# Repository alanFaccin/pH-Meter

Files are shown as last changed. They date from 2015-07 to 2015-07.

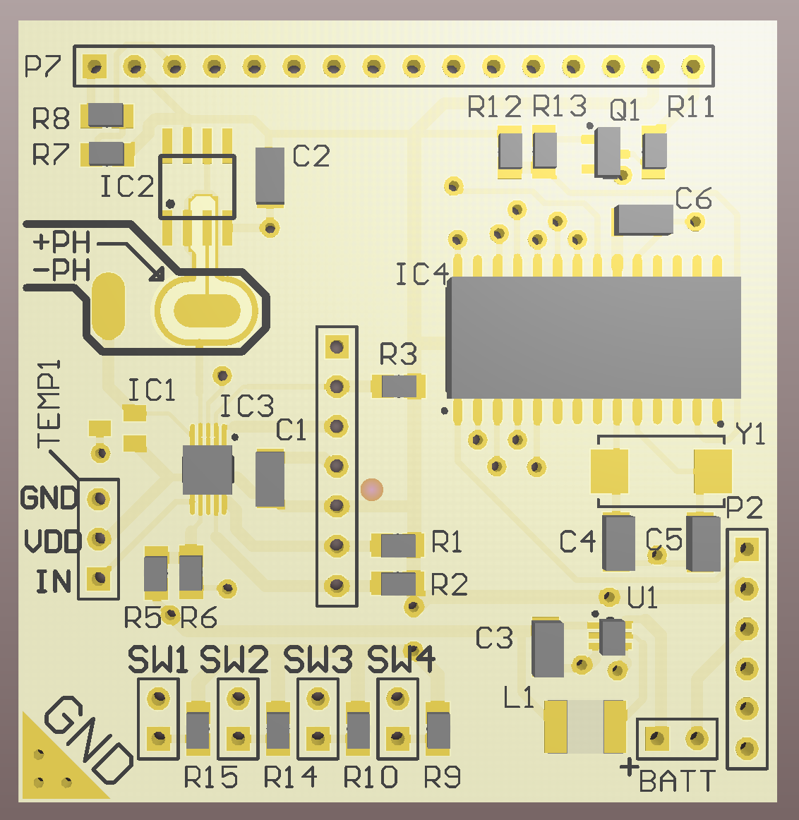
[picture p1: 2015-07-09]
Circuits/export/Schermata 2015-06-11 alle 22.28.34.png

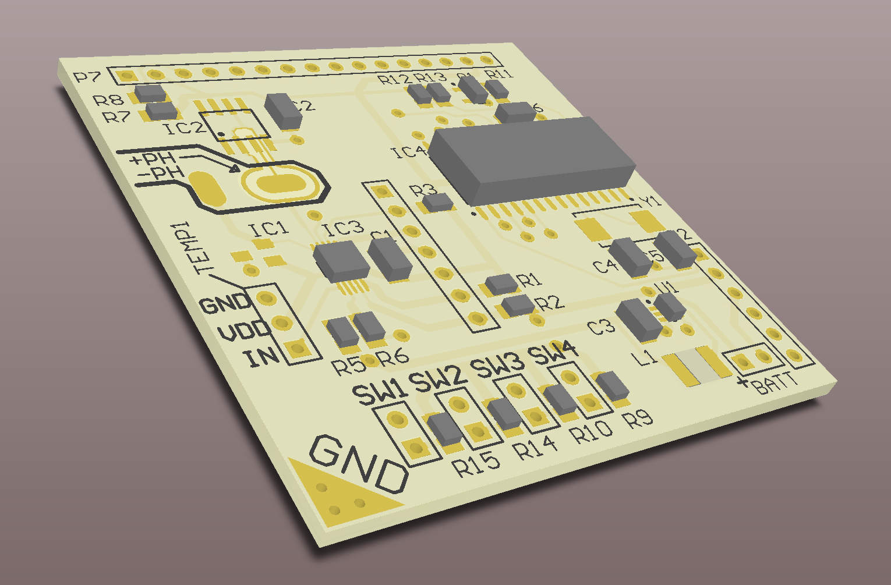
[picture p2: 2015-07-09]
Circuits/export/Schermata 2015-06-11 alle 22.28.52.png

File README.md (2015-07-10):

# pH-Meter

A pH-Meter based on a pic16f876a and a ADS1015 ADC

This project was created as a final year project and thesis.

The purpose of this project is to creare a pH-meter with specifications similar to marketed products.
During development it has been chosen to kept the hardware as modern and concise as possible. When available, modern ICs have been chosen over legacy alternatives, giving space to a state-of-the-art software configurable ADC and ultra-high specs op-amp. [more info in the general hardware description].
The goals of the project were chosen at it’s genesis, and nearly no compromise has been taken during development and design.
An handheld shape has been chosen for the instrument. While a wooden case (CNC machined) is preferred, a 3d printed PLA case is also an available and acceptable solution.

Technical specifications:
• Shape: Handheld tool
• Power source: AA/AAA battery
• Concurrent measurement and display of both pH and temperature • Standard BNC connection for brand-less pH probes
• Temperature resolution better than 0.1°C
• pH resolution of at least 0.1pH
• Easily readable LCD display with firmware control
• Differential measurement mode (delta - Δ)

##license:
A CC-BY-NC-ND Creative Commons license applies

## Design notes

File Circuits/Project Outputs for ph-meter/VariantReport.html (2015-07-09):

Altium customize

# Variant Report

Date | : | 16/06/15
Time | : | 02:15:19
Elapsed Time | : | 00:00:00

## Variations

Physical | Document | Parameter Name | Original Value
C1 | Main_Board.SchDoc | | Fitted
| | Comment
| | Description | Capacitor (Semiconductor SIM Model)
| | Footprint | C1206
| | LatestRevisionDate | 29-May-2009
| | LatestRevisionNote | IPC-7351 Footprint Added.
| | PackageDescription | Chip Capacitor
| | PackageReference | C1206
| | Published | 8-Jun-2000
| | Publisher | Altium Limited
| | Value | 10uF
C2 | Main_Board.SchDoc | | Fitted
| | Comment
| | Description | Capacitor (Semiconductor SIM Model)
| | Footprint | C1206
| | LatestRevisionDate | 29-May-2009
| | LatestRevisionNote | IPC-7351 Footprint Added.
| | PackageDescription | Chip Capacitor
| | PackageReference | C1206
| | Published | 8-Jun-2000
| | Publisher | Altium Limited
| | Value | 10uF
C3 | Main_Board.SchDoc | | Fitted
| | Comment
| | Description | Capacitor (Semiconductor SIM Model)
| | Footprint | C1206
| | LatestRevisionDate | 29-May-2009
| | LatestRevisionNote | IPC-7351 Footprint Added.
| | PackageDescription | Chip Capacitor
| | PackageReference | C1206
| | Published | 8-Jun-2000
| | Publisher | Altium Limited
| | Value | 10uF
C4 | Main_Board.SchDoc | | Fitted
| | Comment
| | Description | Capacitor (Semiconductor SIM Model)
| | Footprint | C1206
| | LatestRevisionDate | 29-May-2009
| | LatestRevisionNote | IPC-7351 Footprint Added.
| | PackageDescription | Chip Capacitor
| | PackageReference | C1206
| | Published | 8-Jun-2000
| | Publisher | Altium Limited
| | Value | 22pF
C5 | Main_Board.SchDoc | | Fitted
| | Comment
| | Description | Capacitor (Semiconductor SIM Model)
| | Footprint | C1206
| | LatestRevisionDate | 29-May-2009
| | LatestRevisionNote | IPC-7351 Footprint Added.
| | PackageDescription | Chip Capacitor
| | PackageReference | C1206
| | Published | 8-Jun-2000
| | Publisher | Altium Limited
| | Value | 22pF
C6 | Main_Board.SchDoc | | Fitted
| | Comment | CAP
| | Description | Capacitor (Semiconductor SIM Model)
| | Footprint | C1206
| | LatestRevisionDate | 29-May-2009
| | LatestRevisionNote | IPC-7351 Footprint Added.
| | PackageDescription | Chip Capacitor
| | PackageReference | C1206
| | Published | 8-Jun-2000
| | Publisher | Altium Limited
| | Value | 100nF
C7 | Main_Board.SchDoc | | Fitted
| | Comment
| | Description | Capacitor (Semiconductor SIM Model)
| | Footprint | C1206
| | LatestRevisionDate | 29-May-2009
| | LatestRevisionNote | IPC-7351 Footprint Added.
| | PackageDescription | Chip Capacitor
| | PackageReference | C1206
| | Published | 8-Jun-2000
| | Publisher | Altium Limited
| | Value | 10uF
H1 | Main_Board.SchDoc | | Fitted
| | Comment | Header 7
| | Description | Header, 7-Pin
| | Footprint | HDR1X7
| | LatestRevisionDate | 17-Jul-2002
| | LatestRevisionNote | Re-released for DXP Platform.
| | Publisher | Altium Limited
IC1 | Main_Board.SchDoc | | Fitted
| | Comment | MAX6101
| | Description | <b> 1.2V Voltage Reference</b> 50ppm/°C, SOT23, 3-Terminal<p> Source: <a href="http://datasheets.maxim-ic.com/en/ds/MAX6520.pdf"> Data sheet </a>
| | Footprint | SOT23
| | MF | MAXIM
| | MPN | MAX6520EUR-T
| | OC_FARNELL | unknown
| | OC_NEWARK | 02J4586
IC2 | Main_Board.SchDoc | | Fitted
| | Comment | LMC6061
| | Description | <b>OP AMP</b>
| | Footprint | SO08
| | V+ | V+
| | V- | V-
IC3 | Main_Board.SchDoc | | Fitted
| | # Input Channels | 4
| | Analog Voltage AV/DD(Max)(V) | 5.5
| | Analog Voltage AV/DD(Min)(V) | 2
| | Architecture | Delta-Sigma
| | Code_JEDEC | MO-153
| | Comment | ADS1015IDGSR
| | ComponentLink1Description | Manufacturer URL
| | ComponentLink1URL | http://www.ti.com/
| | ComponentLink2Description | Datasheet
| | ComponentLink2URL | http://www.ti.com/general/docs/lit/getliterature.tsp?genericPartNumber=ADS1015&fileType=pdf
| | ComponentLink3Description | Package Specification
| | ComponentLink3URL | http://www.ti.com/lit/ml/mpds035b/mpds035b.pdf
| | DatasheetVersion | SBAS473C
| | Description | 12-Bit ADC with Integrated Multiplexer, PGA, Comparator, Oscillator, and Reference, -40 to 125 degC, 10-pin SOP (DGS10), Green (RoHS & no Sb/Br)
| | Digital Supply(Max)(V) | 5.5
| | Digital Supply(Min)(V) | 2
| | Eco-Plan | Green (RoHS & no Sb/Br)
| | Footprint | TI-DGS10_N
| | INL(Max)(+/-LSB) | 0.5
| | Interface | Serial I2C
| | Manufacturer | Texas Instruments
| | Mounting Technology | Surface Mount
| | PackageDescription | 10-Pin Plastic Small Outline, Body 3 x 3 mm, Pitch 0.5 mm
| | PackageReference | DGS10
| | PackageVersion | 4073272/C, 02/2004
| | PartNumber | ADS1015IDGSR
| | Resolution(Bits) | 12
| | Sample Rate (max)(SPS) | 3.3k
| | SubFamily | Precision ADC (<=10MSPS)
| | Supplier 1 | Digi-Key
| | Supplier 2 | Mouser
| | Supplier Part Number 1 | ADS1251U/2K5G4-ND
| | Supplier Part Number 2 | 595-ADS1251U/2K5G4
IC4 | Main_Board.SchDoc | | Fitted
| | # of A/D Channels | 5
| | Comment | PIC16F876-04/SO
| | ComponentLink1Description | Datasheet
| | ComponentLink1URL | http://ww1.microchip.com/downloads/en/DeviceDoc/30292D.pdf
| | ComponentLink2Description | Package Specification
| | ComponentLink2URL | http://www.microchip.com/stellent/groups/techpub_sg/documents/packagingspec/en012702.pdf
| | ComponentLink3Description | URL Link1
| | ComponentLink3URL | Product URL:http://www.microchip.com/datasheet/PIC16F876
| | DatasheetVersion | Rev. D
| | Description | 8-Bit CMOS Flash Microcontroller, 4 MHz, 22 I/O, 0 to 70 degC, 28-pin SOIC (SO28), Tube
| | Digital Communication | 0 -UART, 1 -A/E/USART, 0 -SPI, 0 -I2C, 1 -MSSP(SPI/I2C)
| | EEPROM Data Memory (bytes) | 256
| | Footprint | MCHP-SOIC-SO28_L
| | I/O Pins | 22
| | Manufacturer | Microchip
| | Max. CPU Speed MHz | 4
| | Memory Type | Flash
| | Mounting Technology | Surface Mount
| | Operation Voltage Range | 4V - 5.5V
| | PackageDescription | 28-Lead Plastic Small Outline, 17.9 x 7.5 mm Body, 1.27 mm Pitch
| | PackageReference | SOIC-SO28
| | PackageVersion | C04-052C, 12/2012
| | Packing | TUBE
| | PartNumber | PIC16F876-04/SO
| | Program Memory KBytes | 14
| | Program Memory KWords | 8
| | RAM | 368
| | RoHS | TRUE
| | Supplier 1 | Digi-Key
| | Supplier 2 | Farnell
| | Supplier 3 | Farnell
| | Supplier 4 | Farnell
| | Supplier 5 | Newark
| | Supplier 6 | Mouser
| | Supplier Part Number 1 | PIC16F876-04/SO-ND
| | Supplier Part Number 2 | 9761225MPKG
| | Supplier Part Number 3 | 9761225
| | Supplier Part Number 4 | 1660037
| | Supplier Part Number 5 | 23C5082
| | Supplier Part Number 6 | 579-PIC16F876-04/SO
| | Timers | 2 - 8-bit, 1 - 16-bit
L1 | Main_Board.SchDoc | | Fitted
| | Code_IEC | 1005
| | Code_JEITA | 0402
| | Comment | Inductor
| | Description | Inductor
| | Footprint | INDC4532
| | LatestRevisionDate | 29-May-2009
| | LatestRevisionNote | IPC-7351 Footprint Added.
| | PackageDescription | Chip Inductor
| | PackageReference | 0402-A
| | Published | 8-Jun-2000
| | Publisher | Altium Limited
| | Value | 4.7uH
P1 | Main_Board.SchDoc | | Fitted
| | Comment | Header 2
| | Description | Header, 2-Pin
| | Footprint | HDR1X2
| | LatestRevisionDate | 17-Jul-2002
| | LatestRevisionNote | Re-released for DXP Platform.
| | Publisher | Altium Limited
P2 | Main_Board.SchDoc | | Fitted
| | Comment | Header 6
| | Description | Header, 6-Pin
| | Footprint | HDR1X6
| | LatestRevisionDate | 17-Jul-2002
| | LatestRevisionNote | Re-released for DXP Platform.
| | Publisher | Altium Limited
P3 | Main_Board.SchDoc | | Fitted
| | Comment | Header 2
| | Description | Header, 2-Pin
| | Footprint | HDR1X2
| | LatestRevisionDate | 17-Jul-2002
| | LatestRevisionNote | Re-released for DXP Platform.
| | Publisher | Altium Limited
P4 | Main_Board.SchDoc | | Fitted
| | Comment | Header 2
| | Description | Header, 2-Pin
| | Footprint | HDR1X2
| | LatestRevisionDate | 17-Jul-2002
| | LatestRevisionNote | Re-released for DXP Platform.
| | Publisher | Altium Limited
P5 | Main_Board.SchDoc | | Fitted
| | Comment | Header 2
| | Description | Header, 2-Pin
| | Footprint | HDR1X2
| | LatestRevisionDate | 17-Jul-2002
| | LatestRevisionNote | Re-released for DXP Platform.
| | Publisher | Altium Limited
P6 | Main_Board.SchDoc | | Fitted
| | Comment | Header 2
| | Description | Header, 2-Pin
| | Footprint | HDR1X2
| | LatestRevisionDate | 17-Jul-2002
| | LatestRevisionNote | Re-released for DXP Platform.
| | Publisher | Altium Limited
P7 | Main_Board.SchDoc | | Fitted
| | Comment | Header 16
| | Description | Header, 16-Pin
| | Footprint | HDR1X16
| | LatestRevisionDate | 17-Jul-2002
| | LatestRevisionNote | Re-released for DXP Platform.
| | Publisher | Altium Limited
Q1 | Main_Board.SchDoc | | Fitted
| | Comment | BC846
| | ComponentLink1Description | Manufacturer Link
| | ComponentLink1URL | http://www.semiconductors.philips.com/
| | ComponentLink2Description | Datasheet
| | ComponentLink2URL | http://www.semiconductors.philips.com/acrobat/datasheets/BC846_BC847_BC848_5.pdf
| | DatasheetVersion | 4-Feb-2002
| | Description | NPN General-purpose Transistor
| | Footprint | SOT23_L
| | LatestRevisionDate | 12-Dec-2006
| | LatestRevisionNote | IPC-7351 Footprint Added.
| | PackageDescription | 3-Pin SOT-23 Package 0.95 mm Pitch, 2.3 mm Lead Span
| | PackageReference | SOT23
| | PackageVersion | May-1999
| | Published | 17-Sep-2003
| | Publisher | Altium Limited
R1 | Main_Board.SchDoc | | Fitted
| | Comment | 10K

Description

<p><b>Resistors</b></p> <b>0402</b> - 0402 Surface Mount Package <ul> <li>22 Ohm 1% 1/16W [Digikey: 311-22.0LRTR-ND]</li> <li>33 Ohm 5% 1/16W</li> <li>1.0K 5% 1/16W</li> <li>1.5K 5% 1/16W</li> <li>2.0K 1% 1/16W</li> <li>10.0K 1% 1/16W [Digikey: 311-10.0KLRTR-ND]</li> <li>10.0K 5% 1/16W [Digikey: RMCF0402JT10K0TR-ND]</li> <li>12.1K 1% 1/16W [Digikey: 311-22.0LRTR-ND]</li> <li>100.0K 5% 1/16W</li> </ul> <b>0603</b> - 0603 Surface Mount Package<br> <ul> <li>0 Ohm 1/10 Watt 1% Resistor</li> <li>15 Ohm 1/10 Watt 1% Resistor</li> <li>33 Ohm 1/10 Watt 1% Resistor</li> <li>49.9 Ohm 1/10 Watt 1% Resistor</li> <li>100 Ohm 1/10 Watt 1% Resistor</li> <li>150 Ohm 1/10 Watt 1% Resistor</li> <li>240 Ohm 1/10 Watt 1% Resistor</li> <li>390 Ohm 1/10 Watt 1% Resistor</li> <li>560 Ohm 1/10 Watt 1% Resistor</li> <li>680 Ohm 1/10 Watt 1% Resistor</li> <li>750 Ohm 1/10 Watt 1% Resistor</li> <li>1.0K Ohm 1/10 Watt 1% Resistor</li> <li>1.5K Ohm 1/10 Watt 1% Resistor</li> <li>2.0K Ohm 1/10 Watt 1% Resistor</li> <li>2.2K Ohm 1/10 Watt 1% Resistor</li> <li>3.3K Ohm 1/10 Watt 1% Resistor</li> <li>4.7K Ohm 1/10 Watt 1% Resistor</li> <li>10.0K Ohm 1/10 Watt 1% Resistor</li> <li>12.0K Ohm 1/10 Watt 1% Resistor</li> <li>12.1K Ohm 1/10 Watt 1% Resistor</li> <li>20.0K Ohm 1/10 Watt 1% Resistor</li> <li>33.0K Ohm 1/10 Watt 1% Resistor</li> <li>100.0K Ohm 1/10 Watt 1% Resistor</li> </ul> <b>0805</b> - 0805 Surface Mount Package <ul> <li>0 Ohm 1/8 Watt 1% Resistor</li> <li>33 Ohm 1/8 Watt 1% Resistor</li> <li>100 Ohm 1/8 Watt 1% Resistor</li> <li>150 Ohm 1/8 Watt 1% Resistor</li> <li>200 Ohm 1/8 Watt 1% Resistor</li> <li>240 Ohm 1/8 Watt 1% Resistor</li> <li>330 Ohm 1/8 Watt 1% Resistor</li> <li>390 Ohm 1/8 Watt 1% Resistor</li> <li>470 Ohm 1/8 Watt 1% Resistor</li> <li>1.0K Ohm 1/8 Watt 1% Resistor</li> <li>1.5K Ohm 1/8 Watt 1% Resistor</li> <li>2.0K Ohm 1/8 Watt 1% Resistor</li> <li>4.7K Ohm 1/8 Watt 1% Resistor</li> <li>5.1K Ohm 1/8 Watt 1% Resistor</li> <li>5.6K Ohm 1/8 Watt 1% Resistor</li> <li>10.0K Ohm 1/8 Watt 1% Resistor</li> <li>22.0K Ohm 1/8 Watt 1% Resistor</li> <li>33.0K Ohm 1/8 Watt 1% Resistor</li> <li>100K Ohm 1/8 Watt 1% Resistor</li> </ul> <b>1206</b> - 1206 Surface Mount Package<br/> <br/> <b>2012</b> - 2010 Surface Mount Package<br/> <ul><li>0.11 Ohm 1/2 Watt 1% Resistor - Digikey: RHM.11UCT-ND</li></ul>
| | Footprint | 6-0805_M
R2 | Main_Board.SchDoc | | Fitted
| | Comment | 10K

Description

<p><b>Resistors</b></p> <b>0402</b> - 0402 Surface Mount Package <ul> <li>22 Ohm 1% 1/16W [Digikey: 311-22.0LRTR-ND]</li> <li>33 Ohm 5% 1/16W</li> <li>1.0K 5% 1/16W</li> <li>1.5K 5% 1/16W</li> <li>2.0K 1% 1/16W</li> <li>10.0K 1% 1/16W [Digikey: 311-10.0KLRTR-ND]</li> <li>10.0K 5% 1/16W [Digikey: RMCF0402JT10K0TR-ND]</li> <li>12.1K 1% 1/16W [Digikey: 311-22.0LRTR-ND]</li> <li>100.0K 5% 1/16W</li> </ul> <b>0603</b> - 0603 Surface Mount Package<br> <ul> <li>0 Ohm 1/10 Watt 1% Resistor</li> <li>15 Ohm 1/10 Watt 1% Resistor</li> <li>33 Ohm 1/10 Watt 1% Resistor</li> <li>49.9 Ohm 1/10 Watt 1% Resistor</li> <li>100 Ohm 1/10 Watt 1% Resistor</li> <li>150 Ohm 1/10 Watt 1% Resistor</li> <li>240 Ohm 1/10 Watt 1% Resistor</li> <li>390 Ohm 1/10 Watt 1% Resistor</li> <li>560 Ohm 1/10 Watt 1% Resistor</li> <li>680 Ohm 1/10 Watt 1% Resistor</li> <li>750 Ohm 1/10 Watt 1% Resistor</li> <li>1.0K Ohm 1/10 Watt 1% Resistor</li> <li>1.5K Ohm 1/10 Watt 1% Resistor</li> <li>2.0K Ohm 1/10 Watt 1% Resistor</li> <li>2.2K Ohm 1/10 Watt 1% Resistor</li> <li>3.3K Ohm 1/10 Watt 1% Resistor</li> <li>4.7K Ohm 1/10 Watt 1% Resistor</li> <li>10.0K Ohm 1/10 Watt 1% Resistor</li> <li>12.0K Ohm 1/10 Watt 1% Resistor</li> <li>12.1K Ohm 1/10 Watt 1% Resistor</li> <li>20.0K Ohm 1/10 Watt 1% Resistor</li> <li>33.0K Ohm 1/10 Watt 1% Resistor</li> <li>100.0K Ohm 1/10 Watt 1% Resistor</li> </ul> <b>0805</b> - 0805 Surface Mount Package <ul> <li>0 Ohm 1/8 Watt 1% Resistor</li> <li>33 Ohm 1/8 Watt 1% Resistor</li> <li>100 Ohm 1/8 Watt 1% Resistor</li> <li>150 Ohm 1/8 Watt 1% Resistor</li> <li>200 Ohm 1/8 Watt 1% Resistor</li> <li>240 Ohm 1/8 Watt 1% Resistor</li> <li>330 Ohm 1/8 Watt 1% Resistor</li> <li>390 Ohm 1/8 Watt 1% Resistor</li> <li>470 Ohm 1/8 Watt 1% Resistor</li> <li>1.0K Ohm 1/8 Watt 1% Resistor</li> <li>1.5K Ohm 1/8 Watt 1% Resistor</li> <li>2.0K Ohm 1/8 Watt 1% Resistor</li> <li>4.7K Ohm 1/8 Watt 1% Resistor</li> <li>5.1K Ohm 1/8 Watt 1% Resistor</li> <li>5.6K Ohm 1/8 Watt 1% Resistor</li> <li>10.0K Ohm 1/8 Watt 1% Resistor</li> <li>22.0K Ohm 1/8 Watt 1% Resistor</li> <li>33.0K Ohm 1/8 Watt 1% Resistor</li> <li>100K Ohm 1/8 Watt 1% Resistor</li> </ul> <b>1206</b> - 1206 Surface Mount Package<br/> <br/> <b>2012</b> - 2010 Surface Mount Package<br/> <ul><li>0.11 Ohm 1/2 Watt 1% Resistor - Digikey: RHM.11UCT-ND</li></ul>
| | Footprint | 6-0805_M
R3 | Main_Board.SchDoc | | Fitted
| | Comment | 10K

Description

<p><b>Resistors</b></p> <b>0402</b> - 0402 Surface Mount Package <ul> <li>22 Ohm 1% 1/16W [Digikey: 311-22.0LRTR-ND]</li> <li>33 Ohm 5% 1/16W</li> <li>1.0K 5% 1/16W</li> <li>1.5K 5% 1/16W</li> <li>2.0K 1% 1/16W</li> <li>10.0K 1% 1/16W [Digikey: 311-10.0KLRTR-ND]</li> <li>10.0K 5% 1/16W [Digikey: RMCF0402JT10K0TR-ND]</li> <li>12.1K 1% 1/16W [Digikey: 311-22.0LRTR-ND]</li> <li>100.0K 5% 1/16W</li> </ul> <b>0603</b> - 0603 Surface Mount Package<br> <ul> <li>0 Ohm 1/10 Watt 1% Resistor</li> <li>15 Ohm 1/10 Watt 1% Resistor</li> <li>33 Ohm 1/10 Watt 1% Resistor</li> <li>49.9 Ohm 1/10 Watt 1% Resistor</li> <li>100 Ohm 1/10 Watt 1% Resistor</li> <li>150 Ohm 1/10 Watt 1% Resistor</li> <li>240 Ohm 1/10 Watt 1% Resistor</li> <li>390 Ohm 1/10 Watt 1% Resistor</li> <li>560 Ohm 1/10 Watt 1% Resistor</li> <li>680 Ohm 1/10 Watt 1% Resistor</li> <li>750 Ohm 1/10 Watt 1% Resistor</li> <li>1.0K Ohm 1/10 Watt 1% Resistor</li> <li>1.5K Ohm 1/10 Watt 1% Resistor</li> <li>2.0K Ohm 1/10 Watt 1% Resistor</li> <li>2.2K Ohm 1/10 Watt 1% Resistor</li> <li>3.3K Ohm 1/10 Watt 1% Resistor</li> <li>4.7K Ohm 1/10 Watt 1% Resistor</li> <li>10.0K Ohm 1/10 Watt 1% Resistor</li> <li>12.0K Ohm 1/10 Watt 1% Resistor</li> <li>12.1K Ohm 1/10 Watt 1% Resistor</li> <li>20.0K Ohm 1/10 Watt 1% Resistor</li> <li>33.0K Ohm 1/10 Watt 1% Resistor</li> <li>100.0K Ohm 1/10 Watt 1% Resistor</li> </ul> <b>0805</b> - 0805 Surface Mount Package <ul> <li>0 Ohm 1/8 Watt 1% Resistor</li> <li>33 Ohm 1/8 Watt 1% Resistor</li> <li>100 Ohm 1/8 Watt 1% Resistor</li> <li>150 Ohm 1/8 Watt 1% Resistor</li> <li>200 Ohm 1/8 Watt 1% Resistor</li> <li>240 Ohm 1/8 Watt 1% Resistor</li> <li>330 Ohm 1/8 Watt 1% Resistor</li> <li>390 Ohm 1/8 Watt 1% Resistor</li> <li>470 Ohm 1/8 Watt 1% Resistor</li> <li>1.0K Ohm 1/8 Watt 1% Resistor</li> <li>1.5K Ohm 1/8 Watt 1% Resistor</li> <li>2.0K Ohm 1/8 Watt 1% Resistor</li> <li>4.7K Ohm 1/8 Watt 1% Resistor</li> <li>5.1K Ohm 1/8 Watt 1% Resistor</li> <li>5.6K Ohm 1/8 Watt 1% Resistor</li> <li>10.0K Ohm 1/8 Watt 1% Resistor</li> <li>22.0K Ohm 1/8 Watt 1% Resistor</li> <li>33.0K Ohm 1/8 Watt 1% Resistor</li> <li>100K Ohm 1/8 Watt 1% Resistor</li> </ul> <b>1206</b> - 1206 Surface Mount Package<br/> <br/> <b>2012</b> - 2010 Surface Mount Package<br/> <ul><li>0.11 Ohm 1/2 Watt 1% Resistor - Digikey: RHM.11UCT-ND</li></ul>
| | Footprint | 6-0805_M
R5 | Main_Board.SchDoc | | Fitted
| | Comment | 10K

Description

<p><b>Resistors</b></p> <b>0402</b> - 0402 Surface Mount Package <ul> <li>22 Ohm 1% 1/16W [Digikey: 311-22.0LRTR-ND]</li> <li>33 Ohm 5% 1/16W</li> <li>1.0K 5% 1/16W</li> <li>1.5K 5% 1/16W</li> <li>2.0K 1% 1/16W</li> <li>10.0K 1% 1/16W [Digikey: 311-10.0KLRTR-ND]</li> <li>10.0K 5% 1/16W [Digikey: RMCF0402JT10K0TR-ND]</li> <li>12.1K 1% 1/16W [Digikey: 311-22.0LRTR-ND]</li> <li>100.0K 5% 1/16W</li> </ul> <b>0603</b> - 0603 Surface Mount Package<br> <ul> <li>0 Ohm 1/10 Watt 1% Resistor</li> <li>15 Ohm 1/10 Watt 1% Resistor</li> <li>33 Ohm 1/10 Watt 1% Resistor</li> <li>49.9 Ohm 1/10 Watt 1% Resistor</li> <li>100 Ohm 1/10 Watt 1% Resistor</li> <li>150 Ohm 1/10 Watt 1% Resistor</li> <li>240 Ohm 1/10 Watt 1% Resistor</li> <li>390 Ohm 1/10 Watt 1% Resistor</li> <li>560 Ohm 1/10 Watt 1% Resistor</li> <li>680 Ohm 1/10 Watt 1% Resistor</li> <li>750 Ohm 1/10 Watt 1% Resistor</li> <li>1.0K Ohm 1/10 Watt 1% Resistor</li> <li>1.5K Ohm 1/10 Watt 1% Resistor</li> <li>2.0K Ohm 1/10 Watt 1% Resistor</li> <li>2.2K Ohm 1/10 Watt 1% Resistor</li> <li>3.3K Ohm 1/10 Watt 1% Resistor</li> <li>4.7K Ohm 1/10 Watt 1% Resistor</li> <li>10.0K Ohm 1/10 Watt 1% Resistor</li> <li>12.0K Ohm 1/10 Watt 1% Resistor</li> <li>12.1K Ohm 1/10 Watt 1% Resistor</li> <li>20.0K Ohm 1/10 Watt 1% Resistor</li> <li>33.0K Ohm 1/10 Watt 1% Resistor</li> <li>100.0K Ohm 1/10 Watt 1% Resistor</li> </ul> <b>0805</b> - 0805 Surface Mount Package <ul> <li>0 Ohm 1/8 Watt 1% Resistor</li> <li>33 Ohm 1/8 Watt 1% Resistor</li> <li>100 Ohm 1/8 Watt 1% Resistor</li> <li>150 Ohm 1/8 Watt 1% Resistor</li> <li>200 Ohm 1/8 Watt 1% Resistor</li> <li>240 Ohm 1/8 Watt 1% Resistor</li> <li>330 Ohm 1/8 Watt 1% Resistor</li> <li>390 Ohm 1/8 Watt 1% Resistor</li> <li>470 Ohm 1/8 Watt 1% Resistor</li> <li>1.0K Ohm 1/8 Watt 1% Resistor</li> <li>1.5K Ohm 1/8 Watt 1% Resistor</li> <li>2.0K Ohm 1/8 Watt 1% Resistor</li> <li>4.7K Ohm 1/8 Watt 1% Resistor</li> <li>5.1K Ohm 1/8 Watt 1% Resistor</li> <li>5.6K Ohm 1/8 Watt 1% Resistor</li> <li>10.0K Ohm 1/8 Watt 1% Resistor</li> <li>22.0K Ohm 1/8 Watt 1% Resistor</li> <li>33.0K Ohm 1/8 Watt 1% Resistor</li> <li>100K Ohm 1/8 Watt 1% Resistor</li> </ul> <b>1206</b> - 1206 Surface Mount Package<br/> <br/> <b>2012</b> - 2010 Surface Mount Package<br/> <ul><li>0.11 Ohm 1/2 Watt 1% Resistor - Digikey: RHM.11UCT-ND</li></ul>
| | Footprint | 6-0805_M
R6 | Main_Board.SchDoc | | Fitted
| | Comment | 1K

Description

<p><b>Resistors</b></p> <b>0402</b> - 0402 Surface Mount Package <ul> <li>22 Ohm 1% 1/16W [Digikey: 311-22.0LRTR-ND]</li> <li>33 Ohm 5% 1/16W</li> <li>1.0K 5% 1/16W</li> <li>1.5K 5% 1/16W</li> <li>2.0K 1% 1/16W</li> <li>10.0K 1% 1/16W [Digikey: 311-10.0KLRTR-ND]</li> <li>10.0K 5% 1/16W [Digikey: RMCF0402JT10K0TR-ND]</li> <li>12.1K 1% 1/16W [Digikey: 311-22.0LRTR-ND]</li> <li>100.0K 5% 1/16W</li> </ul> <b>0603</b> - 0603 Surface Mount Package<br> <ul> <li>0 Ohm 1/10 Watt 1% Resistor</li> <li>15 Ohm 1/10 Watt 1% Resistor</li> <li>33 Ohm 1/10 Watt 1% Resistor</li> <li>49.9 Ohm 1/10 Watt 1% Resistor</li> <li>100 Ohm 1/10 Watt 1% Resistor</li> <li>150 Ohm 1/10 Watt 1% Resistor</li> <li>240 Ohm 1/10 Watt 1% Resistor</li> <li>390 Ohm 1/10 Watt 1% Resistor</li> <li>560 Ohm 1/10 Watt 1% Resistor</li> <li>680 Ohm 1/10 Watt 1% Resistor</li> <li>750 Ohm 1/10 Watt 1% Resistor</li> <li>1.0K Ohm 1/10 Watt 1% Resistor</li> <li>1.5K Ohm 1/10 Watt 1% Resistor</li> <li>2.0K Ohm 1/10 Watt 1% Resistor</li> <li>2.2K Ohm 1/10 Watt 1% Resistor</li> <li>3.3K Ohm 1/10 Watt 1% Resistor</li> <li>4.7K Ohm 1/10 Watt 1% Resistor</li> <li>10.0K Ohm 1/10 Watt 1% Resistor</li> <li>12.0K Ohm 1/10 Watt 1% Resistor</li> <li>12.1K Ohm 1/10 Watt 1% Resistor</li> <li>20.0K Ohm 1/10 Watt 1% Resistor</li> <li>33.0K Ohm 1/10 Watt 1% Resistor</li> <li>100.0K Ohm 1/10 Watt 1% Resistor</li> </ul> <b>0805</b> - 0805 Surface Mount Package <ul> <li>0 Ohm 1/8 Watt 1% Resistor</li> <li>33 Ohm 1/8 Watt 1% Resistor</li> <li>100 Ohm 1/8 Watt 1% Resistor</li> <li>150 Ohm 1/8 Watt 1% Resistor</li> <li>200 Ohm 1/8 Watt 1% Resistor</li> <li>240 Ohm 1/8 Watt 1% Resistor</li> <li>330 Ohm 1/8 Watt 1% Resistor</li> <li>390 Ohm 1/8 Watt 1% Resistor</li> <li>470 Ohm 1/8 Watt 1% Resistor</li> <li>1.0K Ohm 1/8 Watt 1% Resistor</li> <li>1.5K Ohm 1/8 Watt 1% Resistor</li> <li>2.0K Ohm 1/8 Watt 1% Resistor</li> <li>4.7K Ohm 1/8 Watt 1% Resistor</li> <li>5.1K Ohm 1/8 Watt 1% Resistor</li> <li>5.6K Ohm 1/8 Watt 1% Resistor</li> <li>10.0K Ohm 1/8 Watt 1% Resistor</li> <li>22.0K Ohm 1/8 Watt 1% Resistor</li> <li>33.0K Ohm 1/8 Watt 1% Resistor</li> <li>100K Ohm 1/8 Watt 1% Resistor</li> </ul> <b>1206</b> - 1206 Surface Mount Package<br/> <br/> <b>2012</b> - 2010 Surface Mount Package<br/> <ul><li>0.11 Ohm 1/2 Watt 1% Resistor - Digikey: RHM.11UCT-ND</li></ul>
| | Footprint | 6-0805_M
R7 | Main_Board.SchDoc | | Fitted
| | Comment | Res3
| | Description | Resistor
| | Footprint | 6-0805_M
| | LatestRevisionDate | 29-May-2009
| | LatestRevisionNote | IPC-7351 Footprint Added.
| | PackageDescription | Chip Resistor
| | PackageReference | J1-0603
| | Published | 8-Jun-2000
| | Publisher | Altium Limited
| | Value | 4K7
R8 | Main_Board.SchDoc | | Fitted
| | Comment | Res3
| | Description | Resistor
| | Footprint | 6-0805_M
| | LatestRevisionDate | 29-May-2009
| | LatestRevisionNote | IPC-7351 Footprint Added.
| | PackageDescription | Chip Resistor
| | PackageReference | J1-0603
| | Published | 8-Jun-2000
| | Publisher | Altium Limited
| | Value | 1K
R9 | Main_Board.SchDoc | | Fitted
| | Comment | Res3
| | Description | Resistor
| | Footprint | 6-0805_M
| | LatestRevisionDate | 29-May-2009
| | LatestRevisionNote | IPC-7351 Footprint Added.
| | PackageDescription | Chip Resistor
| | PackageReference | J1-0603
| | Published | 8-Jun-2000
| | Publisher | Altium Limited
| | Value | 10K
R10 | Main_Board.SchDoc | | Fitted
| | Comment | Res3
| | Description | Resistor
| | Footprint | 6-0805_M
| | LatestRevisionDate | 29-May-2009
| | LatestRevisionNote | IPC-7351 Footprint Added.
| | PackageDescription | Chip Resistor
| | PackageReference | J1-0603
| | Published | 8-Jun-2000
| | Publisher | Altium Limited
| | Value | 10K
R11 | Main_Board.SchDoc | | Fitted
| | Comment | Res3
| | Description | Resistor
| | Footprint | 6-0805_M
| | LatestRevisionDate | 29-May-2009
| | LatestRevisionNote | IPC-7351 Footprint Added.
| | PackageDescription | Chip Resistor
| | PackageReference | J1-0603
| | Published | 8-Jun-2000
| | Publisher | Altium Limited
| | Value | 56
R12 | Main_Board.SchDoc | | Fitted
| | Comment | Res3
| | Description | Resistor
| | Footprint | 6-0805_M
| | LatestRevisionDate | 29-May-2009
| | LatestRevisionNote | IPC-7351 Footprint Added.
| | PackageDescription | Chip Resistor
| | PackageReference | J1-0603
| | Published | 8-Jun-2000
| | Publisher | Altium Limited
| | Value | 1K
R13 | Main_Board.SchDoc | | Fitted
| | Comment | Res3
| | Description | Resistor
| | Footprint | 6-0805_M
| | LatestRevisionDate | 29-May-2009
| | LatestRevisionNote | IPC-7351 Footprint Added.
| | PackageDescription | Chip Resistor
| | PackageReference | J1-0603
| | Published | 8-Jun-2000
| | Publisher | Altium Limited
| | Value | 4K7
R14 | Main_Board.SchDoc | | Fitted
| | Comment | Res3
| | Description | Resistor
| | Footprint | 6-0805_M
| | LatestRevisionDate | 29-May-2009
| | LatestRevisionNote | IPC-7351 Footprint Added.
| | PackageDescription | Chip Resistor
| | PackageReference | J1-0603
| | Published | 8-Jun-2000
| | Publisher | Altium Limited
| | Value | 10K
R15 | Main_Board.SchDoc | | Fitted
| | Comment | Res3
| | Description | Resistor
| | Footprint | 6-0805_M
| | LatestRevisionDate | 29-May-2009
| | LatestRevisionNote | IPC-7351 Footprint Added.
| | PackageDescription | Chip Resistor
| | PackageReference | J1-0603
| | Published | 8-Jun-2000
| | Publisher | Altium Limited
| | Value | 10K
S1 | Main_Board.SchDoc | | Fitted
| | Comment | SW-PB
| | Description | Switch
| | Footprint
| | LatestRevisionDate | 17-Jul-2002
| | LatestRevisionNote | Re-released for DXP Platform.
| | PackageDescription | Switch; 2 Leads
| | PackageReference | SPST-2
| | Published | 24-Mar-1999
| | Publisher | Altium Limited
S2 | Main_Board.SchDoc | | Fitted
| | Comment | SW-PB
| | Description | Switch
| | Footprint
| | LatestRevisionDate | 17-Jul-2002
| | LatestRevisionNote | Re-released for DXP Platform.
| | PackageDescription | Switch; 2 Leads
| | PackageReference | SPST-2
| | Published | 24-Mar-1999
| | Publisher | Altium Limited
S3 | Main_Board.SchDoc | | Fitted
| | Comment | SW-PB
| | Description | Switch
| | Footprint
| | LatestRevisionDate | 17-Jul-2002
| | LatestRevisionNote | Re-released for DXP Platform.
| | PackageDescription | Switch; 2 Leads
| | PackageReference | SPST-2
| | Published | 24-Mar-1999
| | Publisher | Altium Limited
S4 | Main_Board.SchDoc | | Fitted
| | Comment | SW-PB
| | Description | Switch
| | Footprint
| | LatestRevisionDate | 17-Jul-2002
| | LatestRevisionNote | Re-released for DXP Platform.
| | PackageDescription | Switch; 2 Leads
| | PackageReference | SPST-2
| | Published | 24-Mar-1999
| | Publisher | Altium Limited
TEMP1 | Main_Board.SchDoc | | Fitted
| | Comment | Header 3
| | Description | Header, 3-Pin
| | Footprint | HDR1X3
| | LatestRevisionDate | 17-Jul-2002
| | LatestRevisionNote | Re-released for DXP Platform.
| | Publisher | Altium Limited
U1 | Main_Board.SchDoc | | Fitted
| | Code_JEDEC | MO-203-AB
| | Comment | TPS61222DCKR
| | ComponentLink1Description | Datasheet
| | ComponentLink1URL | http://www.ti.com/general/docs/lit/getliterature.tsp?genericPartNumber=TPS61222&fileType=pdf
| | ComponentLink2Description | Package Specification
| | ComponentLink2URL | http://www.ti.com/litv/pdf/mpds114c
| | DatasheetVersion | SLVS776
| | Description | Boost Voltage Converter with 0.7 to 5.5 V Input and 5 V Output, -40 to 85 degC, 6-Pin SC70 (DCK), Green (RoHS & no Sb/Br)
| | Eco-Plan | Green (RoHS & no Sb/Br)
| | Footprint | DCK6_N
| | Manufacturer | Texas Instruments
| | Mounting Technology | Surface Mount
| | PackageDescription | 6-Pin Plastic Small-Outline Package, 2 x 1.3 mm Body, 0.65 mm Pitch, 2.1 mm Lead Span
| | PackageReference | DCK6
| | PackageVersion | revG, Jan-2007
| | PartNumber | TPS61222DCKR
| | Regulated Outputs(#) | 1
| | SubFamily | Step-Up Regulator
| | Supplier 1 | Digi-Key
| | Supplier 2 | Newark
| | Supplier 3 | Mouser
| | Supplier Part Number 1 | TPS61222DCKR-ND
| | Supplier Part Number 2 | 09R6667
| | Supplier Part Number 3 | 595-TPS61222DCKR
| | Switching Frequency(Max)(kHz) | 2000
| | Topology | Boost
| | Vin(Max)(V) | 5.5
| | Vin(Min)(V) | 0.7
| | Vout(Max)(V) | 5
| | Vout(Min)(V) | 5
Y1 | Main_Board.SchDoc | | Fitted
| | Comment | 16Mhz
| | ComponentLink1Description | Manufacturer Link
| | ComponentLink1URL | http://www.cmac.com/mt/
| | ComponentLink2Description | Datasheet
| | ComponentLink2URL | http://www.cmac.com/mt/databook/crystals/smd/3smx.pdf
| | DatasheetDocument | 6-Apr-1998
| | Description | Surface Mount Quartz Crystal
| | Footprint | CFPX-93
| | Note | PCB layout complies with manufacturer's recommendation.
| | PackageDocument | 6-Apr-1998
| | PackageReference | 3SMXA
| | Published | 17-Jul-2002
| | Publisher | Altium Limited

Back to top

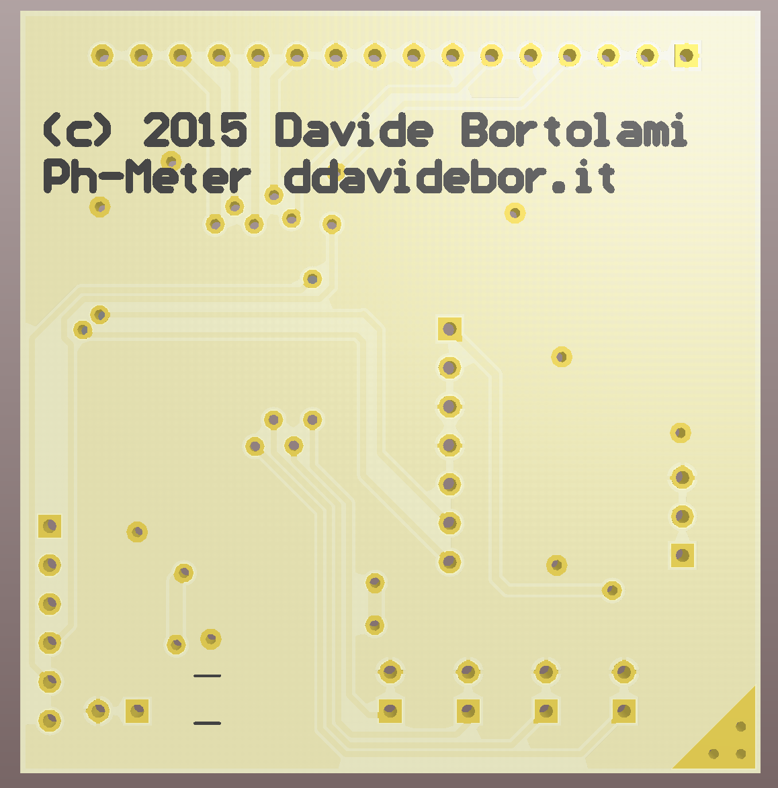
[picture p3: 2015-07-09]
Circuits/export/Schermata 2015-06-11 alle 22.29.11.png

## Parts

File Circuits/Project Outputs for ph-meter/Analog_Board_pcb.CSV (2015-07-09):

Bill of Material for
On 11/06/15 at 22:24:15
Comment | Pattern | Quantity | Components
 | C1206 | 5 | C1, C2, C3, C4, C5 | Capacitor (Semiconductor SIM Model)
10K | 6-0805_M | 4 | R1, R2, R3, R5 | <p><b>Resistors</b></p> <b>0402</b> - 0402 Surface Mount Package <ul> <li>22 Ohm 1% 1/16W [Digikey: 311-22.0LRTR-ND]</li> <li>33 Ohm 5% 1/16W</li> <li>1.0K 5% 1/16W</li> <li>1.5K 5% 1/16W</li> <li>2.0K 1% 1/16W</li> <li>10.0K 1% 1/16W [Digikey: 311-10.0KLRTR-ND]</li> <li>10.0K 5% 1/16W [Digikey: RMCF0402JT10K0TR-ND]</li> <li>12.1K 1% 1/16W [Digikey: 311-22.0LRTR-ND]</li> <li>100.0K 5% 1/16W</li> </ul> <b>0603</b> - 0603 Surface Mount Package<br> <ul> <li>0 Ohm 1/10 Watt 1% Resistor</li> <li>15 Ohm 1/10 Watt 1% Resistor</li> <li>33 Ohm 1/10 Watt 1% Resistor</li> <li>49.9 Ohm 1/10 Watt 1% Resistor</li> <li>100 Ohm 1/10 Watt 1% Resistor</li> <li>150 Ohm 1/10 Watt 1% Resistor</li> <li>240 Ohm 1/10 Watt 1% Resistor</li> <li>390 Ohm 1/10 Watt 1% Resistor</li> <li>560 Ohm 1/10 Watt 1% Resistor</li> <li>680 Ohm 1/10 Watt 1% Resistor</li> <li>750 Ohm 1/10 Watt 1% Resistor</li> <li>1.0K Ohm 1/10 Watt 1% Resistor</li> <li>1.5K Ohm 1/10 Watt 1% Resistor</li> <li>2.0K Ohm 1/10 Watt 1% Resistor</li> <li>2.2K Ohm 1/10 Watt 1% Resistor</li> <li>3.3K Ohm 1/10 Watt 1% Resistor</li> <li>4.7K Ohm 1/10 Watt 1% Resistor</li> <li>10.0K Ohm 1/10 Watt 1% Resistor</li> <li>12.0K Ohm 1/10 Watt 1% Resistor</li> <li>12.1K Ohm 1/10 Watt 1% Resistor</li> <li>20.0K Ohm 1/10 Watt 1% Resistor</li> <li>33.0K Ohm 1/10 Watt 1% Resistor</li> <li>100.0K Ohm 1/10 Watt 1% Resistor</li> </ul> <b>0805</b> - 0805 Surface Mount Package <ul> <li>0 Ohm 1/8 Watt 1% Resistor</li> <li>33 Ohm 1/8 Watt 1% Resistor</li> <li>1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
16Mhz | CFPX-93 | 1 | Y1 | Surface Mount Quartz Crystal
1K | 6-0805_M | 1 | R6 | <p><b>Resistors</b></p> <b>0402</b> - 0402 Surface Mount Package <ul> <li>22 Ohm 1% 1/16W [Digikey: 311-22.0LRTR-ND]</li> <li>33 Ohm 5% 1/16W</li> <li>1.0K 5% 1/16W</li> <li>1.5K 5% 1/16W</li> <li>2.0K 1% 1/16W</li> <li>10.0K 1% 1/16W [Digikey: 311-10.0KLRTR-ND]</li> <li>10.0K 5% 1/16W [Digikey: RMCF0402JT10K0TR-ND]</li> <li>12.1K 1% 1/16W [Digikey: 311-22.0LRTR-ND]</li> <li>100.0K 5% 1/16W</li> </ul> <b>0603</b> - 0603 Surface Mount Package<br> <ul> <li>0 Ohm 1/10 Watt 1% Resistor</li> <li>15 Ohm 1/10 Watt 1% Resistor</li> <li>33 Ohm 1/10 Watt 1% Resistor</li> <li>49.9 Ohm 1/10 Watt 1% Resistor</li> <li>100 Ohm 1/10 Watt 1% Resistor</li> <li>150 Ohm 1/10 Watt 1% Resistor</li> <li>240 Ohm 1/10 Watt 1% Resistor</li> <li>390 Ohm 1/10 Watt 1% Resistor</li> <li>560 Ohm 1/10 Watt 1% Resistor</li> <li>680 Ohm 1/10 Watt 1% Resistor</li> <li>750 Ohm 1/10 Watt 1% Resistor</li> <li>1.0K Ohm 1/10 Watt 1% Resistor</li> <li>1.5K Ohm 1/10 Watt 1% Resistor</li> <li>2.0K Ohm 1/10 Watt 1% Resistor</li> <li>2.2K Ohm 1/10 Watt 1% Resistor</li> <li>3.3K Ohm 1/10 Watt 1% Resistor</li> <li>4.7K Ohm 1/10 Watt 1% Resistor</li> <li>10.0K Ohm 1/10 Watt 1% Resistor</li> <li>12.0K Ohm 1/10 Watt 1% Resistor</li> <li>12.1K Ohm 1/10 Watt 1% Resistor</li> <li>20.0K Ohm 1/10 Watt 1% Resistor</li> <li>33.0K Ohm 1/10 Watt 1% Resistor</li> <li>100.0K Ohm 1/10 Watt 1% Resistor</li> </ul> <b>0805</b> - 0805 Surface Mount Package <ul> <li>0 Ohm 1/8 Watt 1% Resistor</li> <li>33 Ohm 1/8 Watt 1% Resistor</li> <li>1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
ADS1015IDGSR | TI-DGS10_N | 1 | IC3 | 12-Bit ADC with Integrated Multiplexer, PGA, Comparator, Oscillator, and Reference, -40 to 125 degC, 10-pin SOP (DGS10), Green (RoHS & no Sb/Br)
BC846 | SOT23_L | 1 | Q1 | NPN General-purpose Transistor
Cap Semi | C1206 | 1 | C6 | Capacitor (Semiconductor SIM Model)
Header 16 | HDR1X16 | 1 | P7 | Header, 16-Pin
Header 2 | HDR1X2 | 5 | BATT, SW1, SW2, SW3, SW4 | Header, 2-Pin
Header 3 | HDR1X3 | 1 | TEMP1 | Header, 3-Pin
Header 6 | HDR1X6 | 1 | P2 | Header, 6-Pin
Header 7 | HDR1X7 | 1 | H1 | Header, 7-Pin
Inductor | INDC4532 | 1 | L1 | Inductor
LMC6061 | SO08 | 1 | IC2 | <b>OP AMP</b>
MAX6101 | SOT23 | 1 | IC1 | <b> 1.2V Voltage Reference</b> 50ppm/°C, SOT23, 3-Terminal<p> Source: <a href=http://datasheets.maxim-ic.com/en/ds/MAX6520.pdf"> Data sheet </a>"
PIC16F876-04/SO | MCHP-SOIC-SO28_L | 1 | IC4 | 8-Bit CMOS Flash Microcontroller, 4 MHz, 22 I/O, 0 to 70 degC, 28-pin SOIC (SO28), Tube
Res3 | 6-0805_M | 9 | R7, R8, R9, R10, R11, R12, R13, R14, R15 | Resistor
TPS61222DCKR | DCK6_N | 1 | U1 | Boost Voltage Converter with 0.7 to 5.5 V Input and 5 V Output, -40 to 85 degC, 6-Pin SC70 (DCK), Green (RoHS & no Sb/Br)

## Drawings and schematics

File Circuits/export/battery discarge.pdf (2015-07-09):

Constant Power Performance | Constant Current Performance

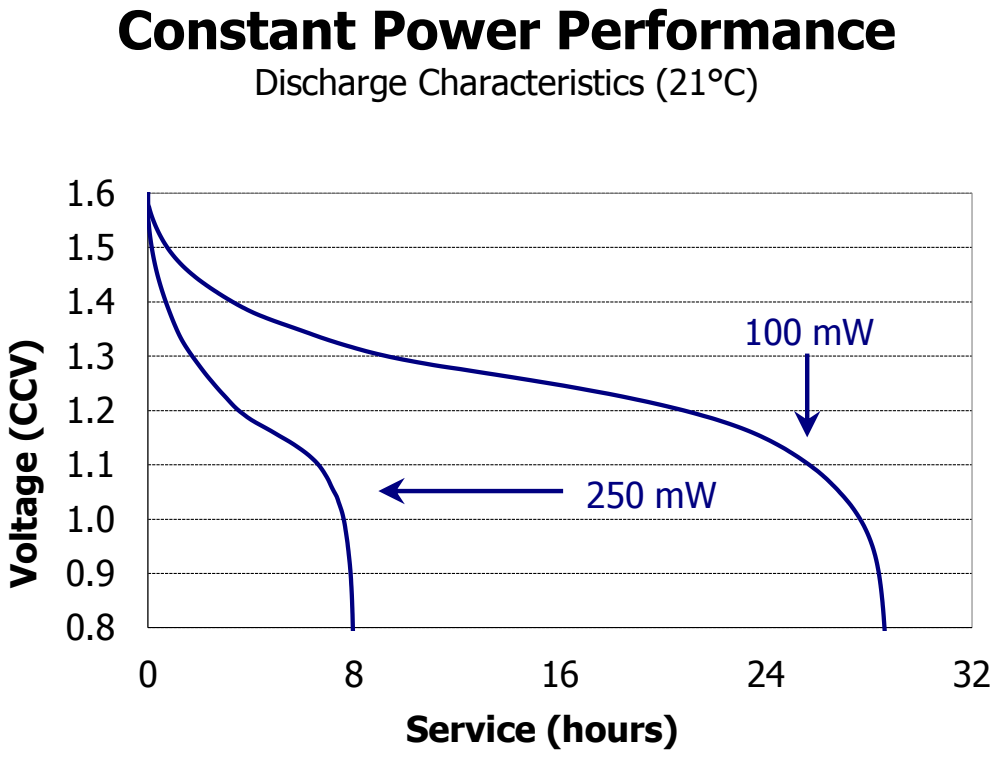
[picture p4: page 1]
Discharge Characteristics (21°C); Voltage (CCV); Service (hours)

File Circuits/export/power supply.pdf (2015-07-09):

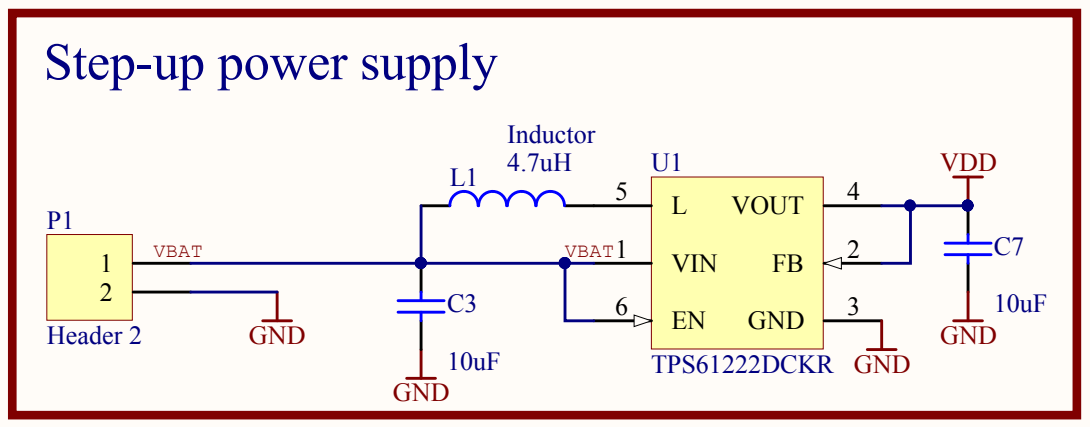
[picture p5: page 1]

Step-up power supply

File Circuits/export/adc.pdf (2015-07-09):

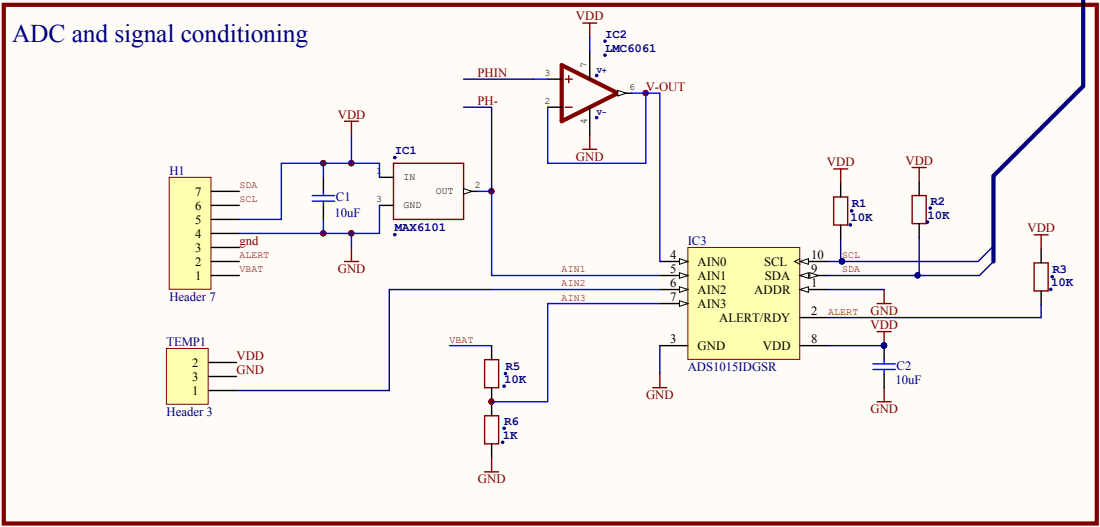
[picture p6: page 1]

ADC and signal conditioning

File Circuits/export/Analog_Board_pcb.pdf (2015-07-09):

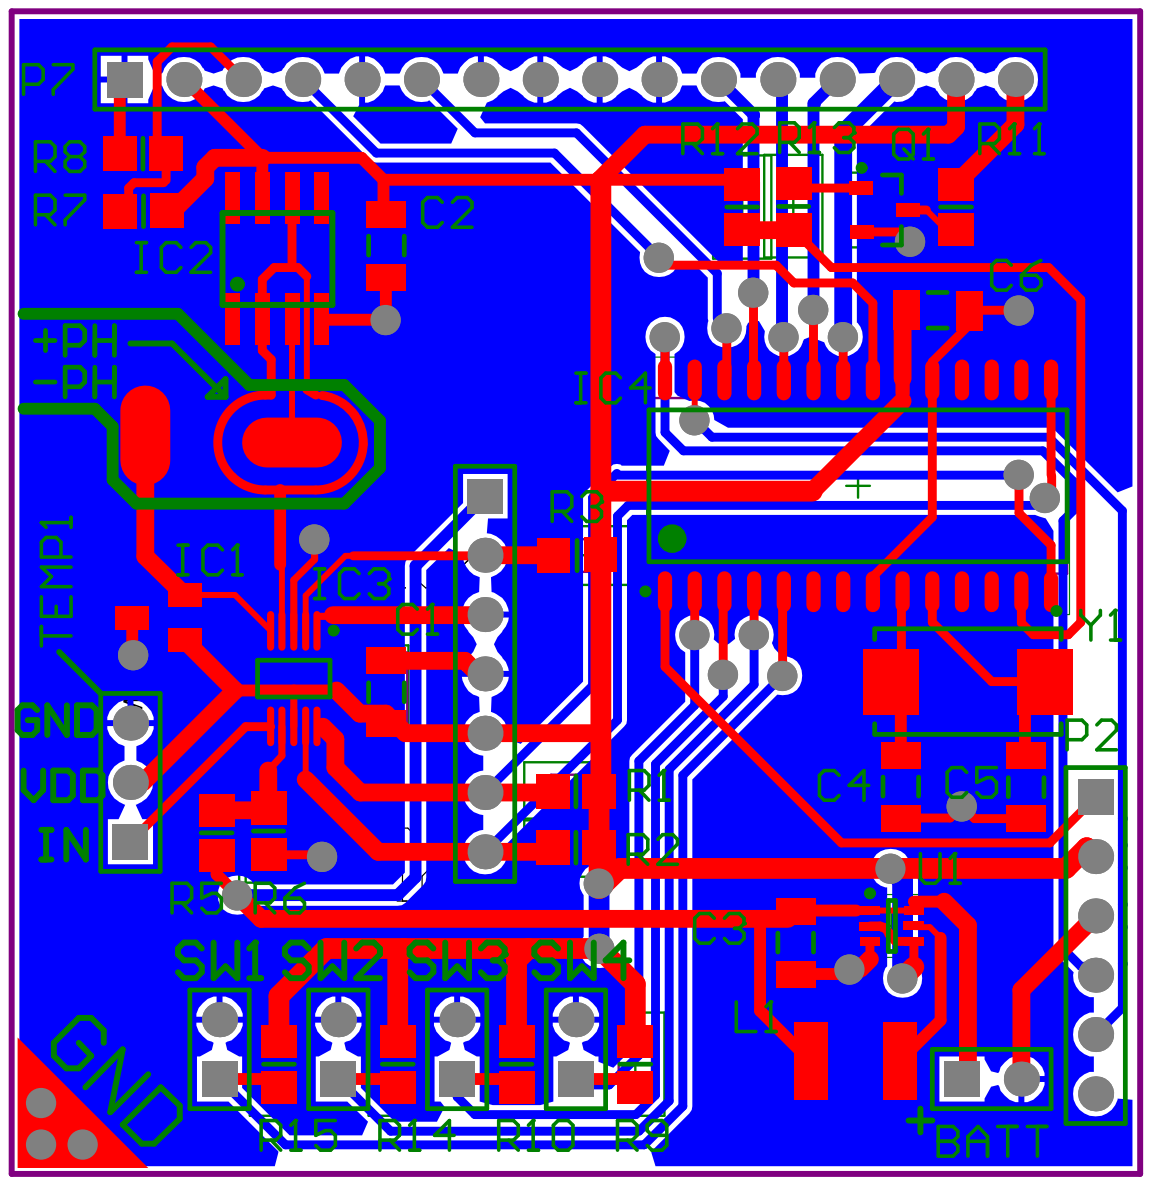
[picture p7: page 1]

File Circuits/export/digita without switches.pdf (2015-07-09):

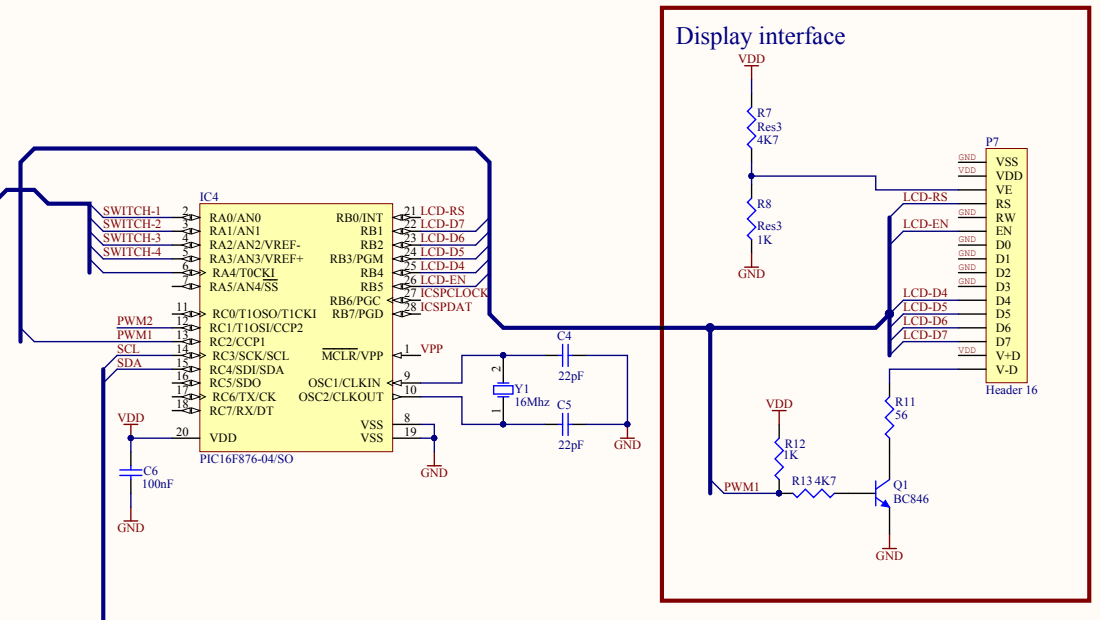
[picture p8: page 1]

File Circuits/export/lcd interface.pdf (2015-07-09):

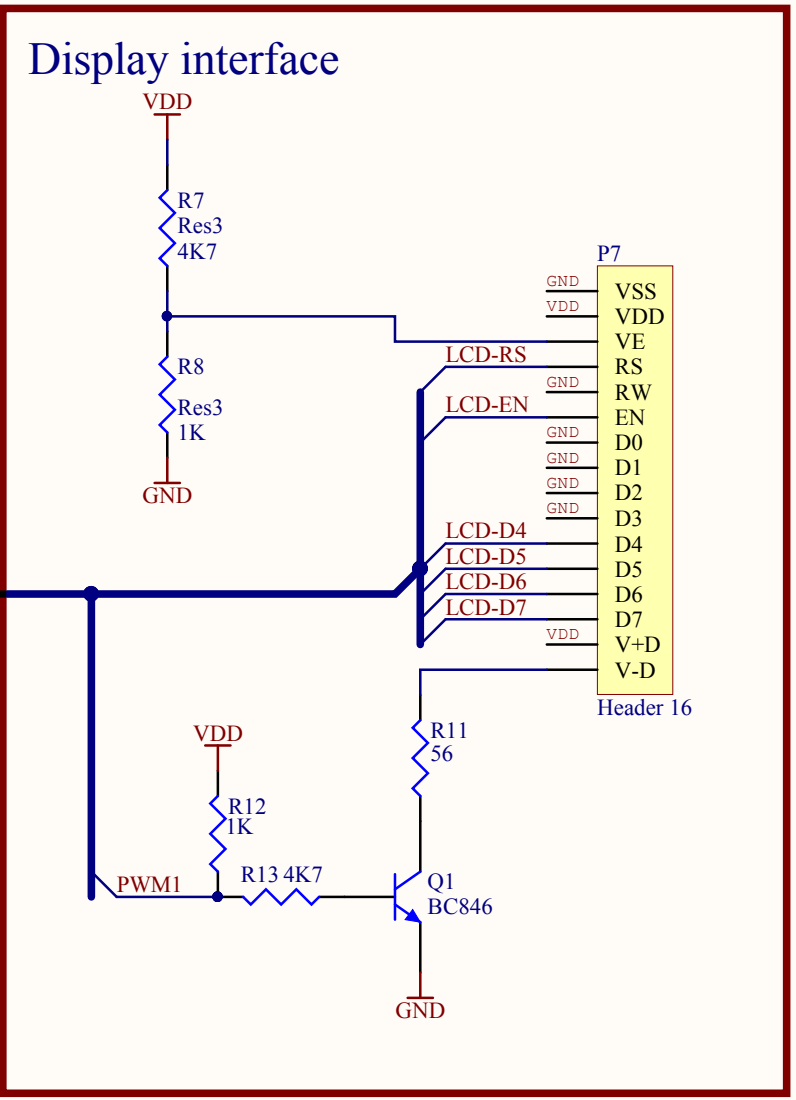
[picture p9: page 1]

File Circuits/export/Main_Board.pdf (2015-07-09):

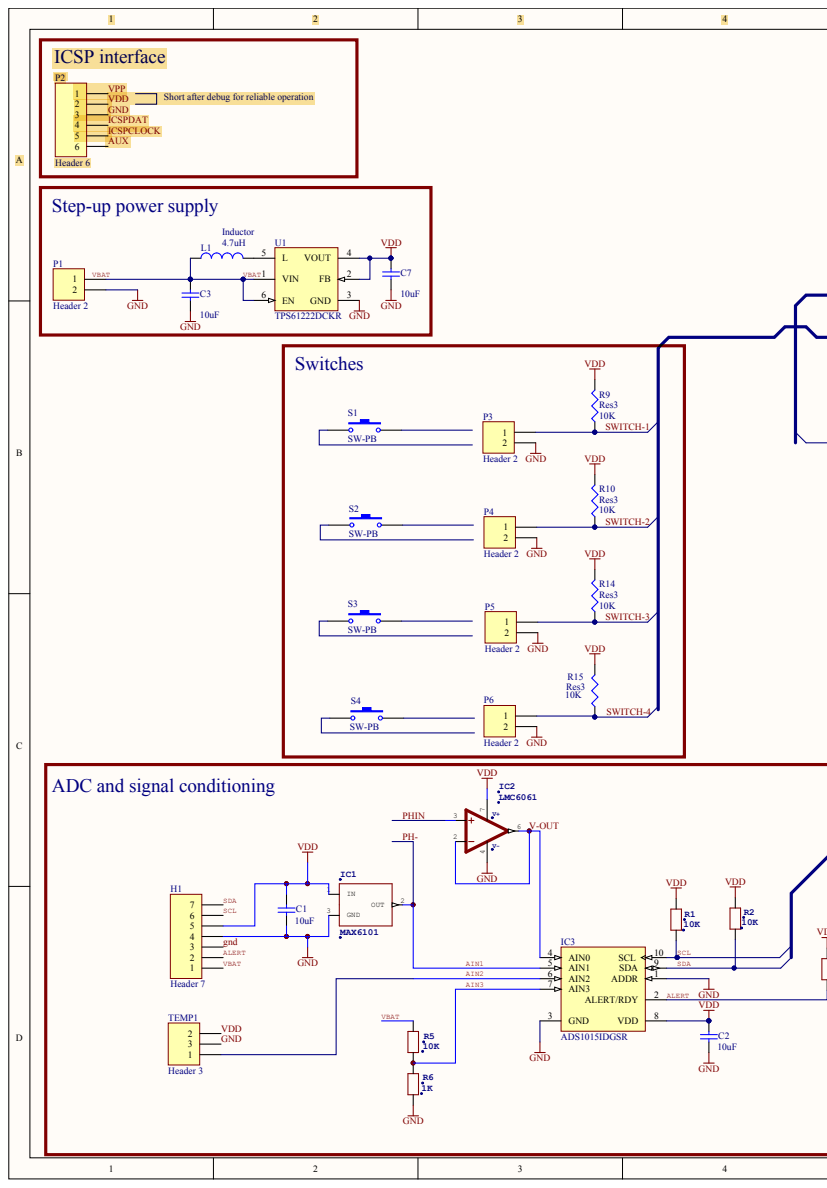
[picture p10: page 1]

Short after debug for reliable operation VPP
VDD
GND
ICSPDAT
ICSPCLOCK
AUX

ADC and signal conditioning

2 | GND

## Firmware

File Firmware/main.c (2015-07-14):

/*
PH METER BY DAVIDE BORTOLAMI
ALL RIGHT RESERVED (C) 2015 Davide Bortolami
 *
 * Made for pic16f876A
 * I.T.I. "F. Severi" Padua
 *
 */

//define Board_EasyPicV7
//#define Board_SeveriDemoLCD
#define Board_PCBFinal


//pic configuration - must be the first include
#include "libraries/conf_and_includes/configuration.h"
//general c includes
#include "libraries/conf_and_includes/includes.h"


//board specific library and main include files
#include "libraries/board-specific/easypic-v7-pic16.h"
//lcd library
#include "libraries/lcd/LCD.h"
//physical constant library
#include "libraries/physics/constants.h"
//ads-1015 library with mask for config bytes
#include "libraries/ads1015/ads1015-config.h"
//pwm library
#include "libraries/pwm/pwm.h"
//hardware i2c library
#include "libraries/i2c/i2cb.h"
//routine for ads1015 acquisition
#include "libraries/ads1015/ads1015_routines.h"
//temperature conversion library
#include "libraries/physics/temperature_conv.h"

//change backlight everytime the subroutine is called
void Backlight_Setup(char reset)
{

    static unsigned int backlight;

    for(char i=0; i<250; i++)
    {
        backlight ++;
        if(backlight < 1023)
            PWM1_Duty(backlight);
    }

    if (backlight >= 1022)
        backlight = 0;

    
    if(reset)
        backlight = 0;

    PWM1_Duty(backlight);
    __delay_ms(100);

}

//setup subroutine, to be called once
void setup(void) {

    //tris configuration
    TRISA = 0b11111111;
    TRISB = 0b11000000;
    TRISC = 0b11100001;

    //port initialization
    PORTA = 0x00;
    PORTB = 0x00;
    PORTC = 0x00;

    ADCON1 = 0b00000110;
    
    //libraries initialization
    LCD_Init();
    PWM_Init(5000);
    I2CInit();

    //reset lcd to initial position and clear
    LCD_Clear();
    LCD_Set_Cursor(1,1);

    //create a custom delta (uppercase greek letter) simbol
    //const declaration allow RAM to be preserved
    const char delta_array[8] = {0x4,0xe,0xa,0x1b,0x11,0x11,0x1f,0x0};  
    LCD_Custom_Char(delta_array, 0x00);

    PWM1_Start();
    PWM1_Duty(0);
    //boot screen - can be activated/deactivated in configuration.h
    if(BOOT_SCREEN)
    {
        //boot text
        LCD_Set_Cursor(1, 1);
        LCD_Write_String("    Ph-Meter   ");
        LCD_Set_Cursor(2, 1);
        LCD_Write_String("By ddavidebor.it");

        //smooth backlight power-up
        for(int  i=0; i!=1022; i+=2)
        {
            __delay_ms(1);
            PWM1_Duty(i);
        }


        //two backlight flash
        PWM1_Stop();
        PORTCbits.RC2 = 1;
        __delay_ms(120);
        PORTCbits.RC2 = 0;
        __delay_ms(120);
        PORTCbits.RC2 = 1;
        __delay_ms(120);
        PORTCbits.RC2 = 0;
        __delay_ms(120);
        PORTCbits.RC2 = 1;
        
        __delay_ms(700);
        LCD_Clear();

        LCD_Set_Cursor(1,1);
        }

    Backlight_Setup(true);

    
    PWM1_Start();
    PWM1_Duty(Backlight_default_pwm);

    

}

//Calculate ph based on voltage (V) and temperature (°K)
float PhCalc(float Voltage, float Temperature) {

    //Voltage imput must be absolute, with zero on 0, positive or negative
    float Ph = 0;
    Ph = 7 + (Voltage * CONST_FARADAY) / (CONST_MOLAR_GAS * Temperature * CONST_TENTH_LINEAR_LOG);
    return Ph;

}

//Return temperature in celsius degrees
float GetTemperature_celsius(void)
{
    return ( 100 * VoltageReadSingleEnded(2, RANGE_1_024V));
}

//Get battery voltage in percentage
unsigned char GetBattery_percent()
{
    //return (Rbottom/Rtop)*100*Vout/VBattMax
    return (11*100*VoltageReadSingleEnded(3, RANGE_1_024V))/BATTERY_VOLTAGE;
}

//Print a float on the lcd in the form of 12.34
//This part of code should be deprecated after testing is concluded
void print_float(float value){

    unsigned int integer_part;
    integer_part = trunc(value);
  
    unsigned int floating_part;
    floating_part = ((value - integer_part)*100);
    if (value > 0)
        LCD_Write_Char(' ');
    else
    {
        integer_part = -integer_part;
        floating_part = -floating_part;
        LCD_Write_Char('-');
    }
    LCD_printf("%2d.%02d", integer_part, floating_part);
}

//Check if the probe voltage is within reasonable parameters
void error_diagnostics_ph_probe_overload(float voltage)
{
    static float minimun = -probe_voltage_overload;
    static float maximun =  probe_voltage_overload;

    //if voltage is ok return
    if ((voltage < maximun) && (voltage > minimun))
        return;

    LCD_Clear();

    LCD_Set_Cursor(1, 1);
    LCD_printf("    Ph probe    ");

    LCD_Set_Cursor(2, 1);
    LCD_printf("    overload   ");

    for(char i=0; i!=5; i++)
    {
        __delay_ms(350);
        LCD_Power(false);
        __delay_ms(350);
        LCD_Power(true);
    }

    LCD_Power(true);
    LCD_Clear();
    
}

//Check if the temperature read is within parameters
void error_diagnostics_temperature_overload(float temperature)
{
    static float maximun = 100.0;
    //if temperature is ok return
    if (temperature < maximun)
        return;

    LCD_Clear();

    LCD_Set_Cursor(1, 1);
    LCD_printf("   Temp probe   ");

    LCD_Set_Cursor(2, 1);
    LCD_printf("    overload   ");

    for(char i=0; i!=5; i++)
    {
        __delay_ms(350);
        LCD_Power(false);
        __delay_ms(350);
        LCD_Power(true);
    }

    LCD_Power(true);
    LCD_Clear();


}


//Print the main mode, featuring ph, temperature and battery
void print_main(float ph_print, float temperature_print, char battery_print) {

        //LCD_Clear();
        int integer_part;
        int floating_part;
        char tempchar;

        //printf first row
        LCD_Set_Cursor(1, 1);
        integer_part = trunc(ph_print); //trunc() truncate the number and return only the integer part without aproximation
        floating_part = ((ph_print - integer_part)*100);

        LCD_printf("Ph %2d.%02d || BATT", integer_part, floating_part);
        

        //print second row
        LCD_Set_Cursor(2, 1);
        integer_part = trunc(temperature_print);
        floating_part = ((temperature_print - integer_part)*10);

        LCD_printf("%cC %2d.%01d  || %3d%%", 0xDF, integer_part, floating_part, battery_print);

}

//Print delta mode, featuring delta, initial ph, temperature and battery
void print_delta(float ph_zero, float ph_delta, float temperature_print, char battery_print )
{

        int integer_part;
        int floating_part;

        //printf first row
        LCD_Set_Cursor(1, 1);
        integer_part = trunc(ph_delta); //trunc() truncate the number and return only the integer part without aproximation
        floating_part = ((ph_delta - integer_part)*100);
        char tempchar;
        if (ph_delta > 0)
            tempchar = ' ';
        else
        {
            integer_part = -integer_part;
            floating_part = -floating_part;
            tempchar='-';
        }
        LCD_Write_Char(0x00); //write delta
        LCD_printf("Ph %c%2d.%02d |BATT", tempchar, integer_part, floating_part);

        //print second row
        LCD_Set_Cursor(2, 1);
        integer_part = trunc(ph_zero);
        floating_part = ((ph_zero - integer_part)*100);
        LCD_printf("Ph0  %2d.%02d |%3d%%",  integer_part, floating_part, battery_print);

}


//One univoque char for every mode
#define MODE_MAIN 0x01 //main mode
#define MODE_DELTA 0x02 //delta mode
#define MODE_DEBUG_VOLTAGE 0x03 //voltage from adc, only for debug


void MODE_Main( long unsigned int cycle_counter)
{
     float voltage;
     float temperature;
     float ph;
     char battery;

     static float ph_array[6]; //array used for mean
     const char measurement_cycles = 5;  //number of measurement per LCD writes

     //clear lcd upon mode activation
     if (cycle_counter == 0)
         LCD_Clear();

     temperature = GetTemperature_celsius();
     voltage = GetProbe_voltage();
     battery = GetBattery_percent();

     //check for errors and overloads
     error_diagnostics_ph_probe_overload(voltage);
     error_diagnostics_temperature_overload(temperature);


     //calculate ph
     ph = PhCalc(voltage, CelsiusToKelvin(temperature));

     //print every tot cycles
     ph_array[cycle_counter % measurement_cycles] = ph;
     if((cycle_counter % measurement_cycles )==0)
     {
         ph = 0;
         for(char i=0; i!=measurement_cycles; i++)
             ph+=ph_array[i];
         ph=ph/measurement_cycles;
         print_main(ph, temperature, battery);
     }

        
}

//Mode for delta measurement
void MODE_Delta(long unsigned int cycle_counter)
{
     static float ph_zero;
     float voltage;
     float temperature;
     char battery;
     float ph_delta;

     static float ph_array[6]; //array used for mean
     const char measurement_cycles = 5;  //number of measurement per LCD writes


     temperature = GetTemperature_celsius();
     voltage = GetProbe_voltage();
     battery = GetBattery_percent();

     //check for errors and overloads
     error_diagnostics_ph_probe_overload(voltage);
     error_diagnostics_temperature_overload(temperature);

     //if button has just been pressed
     if(cycle_counter==0)
     {
         LCD_Clear();
         //acquire ph-zero
         ph_zero = PhCalc(voltage, CelsiusToKelvin(temperature));
     }

     ph_delta = PhCalc(voltage, CelsiusToKelvin(temperature)) - ph_zero;


     ph_array[cycle_counter % measurement_cycles] = ph_delta;
     if((cycle_counter % measurement_cycles )==0)
     {
         ph_delta = 0;
         for(char i=0; i!=measurement_cycles; i++)
             ph_delta+=ph_array[i];
         ph_delta=ph_delta/measurement_cycles;
     print_delta(ph_zero,ph_delta,CelsiusToKelvin(temperature),battery );

     }


}

//Show some useful voltage read from the ph probe sensor
void MODE_Debug_Voltage(long unsigned int cycle_counter)
{
     if(cycle_counter==0)
     LCD_Clear();

     //ra2 as voltage, divided by five
     //assuming temperature = 25°c

     float voltage[4];
     voltage[0] = VoltageReadSingleEnded(0, RANGE_4_096V);
     voltage[1] = VoltageReadSingleEnded(1, RANGE_4_096V);
     voltage[2] = VoltageReadSingleEnded(2, RANGE_4_096V);
     voltage[3] = VoltageReadSingleEnded(3, RANGE_4_096V);

     LCD_Set_Cursor(1,1);
     LCD_Write_Char('S');
     LCD_Write_Char(' ');
     print_float(voltage[0]);
     LCD_Write_Char('R');
     LCD_Write_Char(' ');
     print_float(voltage[1]);
     LCD_Set_Cursor(2,1);
     LCD_printf("Diff:    ");
     print_float(GetProbe_voltage());
     LCD_Write_Char('V');

}
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
